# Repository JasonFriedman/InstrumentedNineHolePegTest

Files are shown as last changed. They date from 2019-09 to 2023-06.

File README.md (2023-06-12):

# InstrumentedNineHolePegTest
An instrumented version (i.e., with sensors) of the nine hole peg test

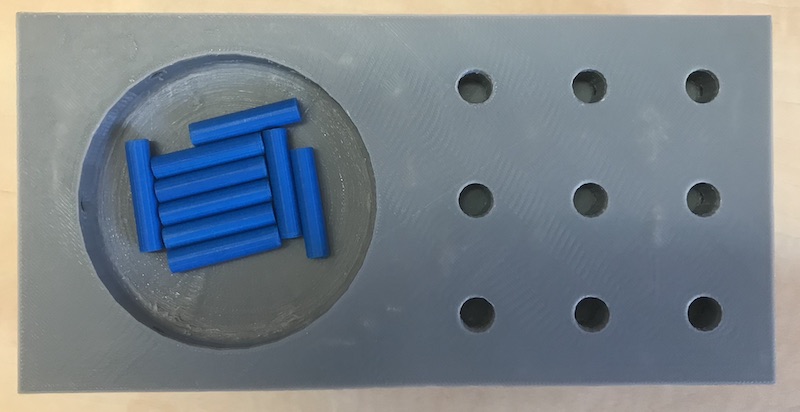
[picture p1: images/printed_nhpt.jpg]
Picture of the 3D printed device


Details about how to build the test can be found in the 
[wiki](https://github.com/JasonFriedman/InstrumentedNineHolePegTest/wiki)



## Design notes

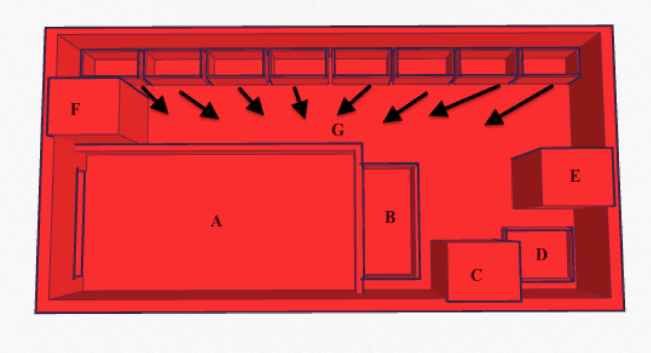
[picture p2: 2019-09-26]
images/base.png

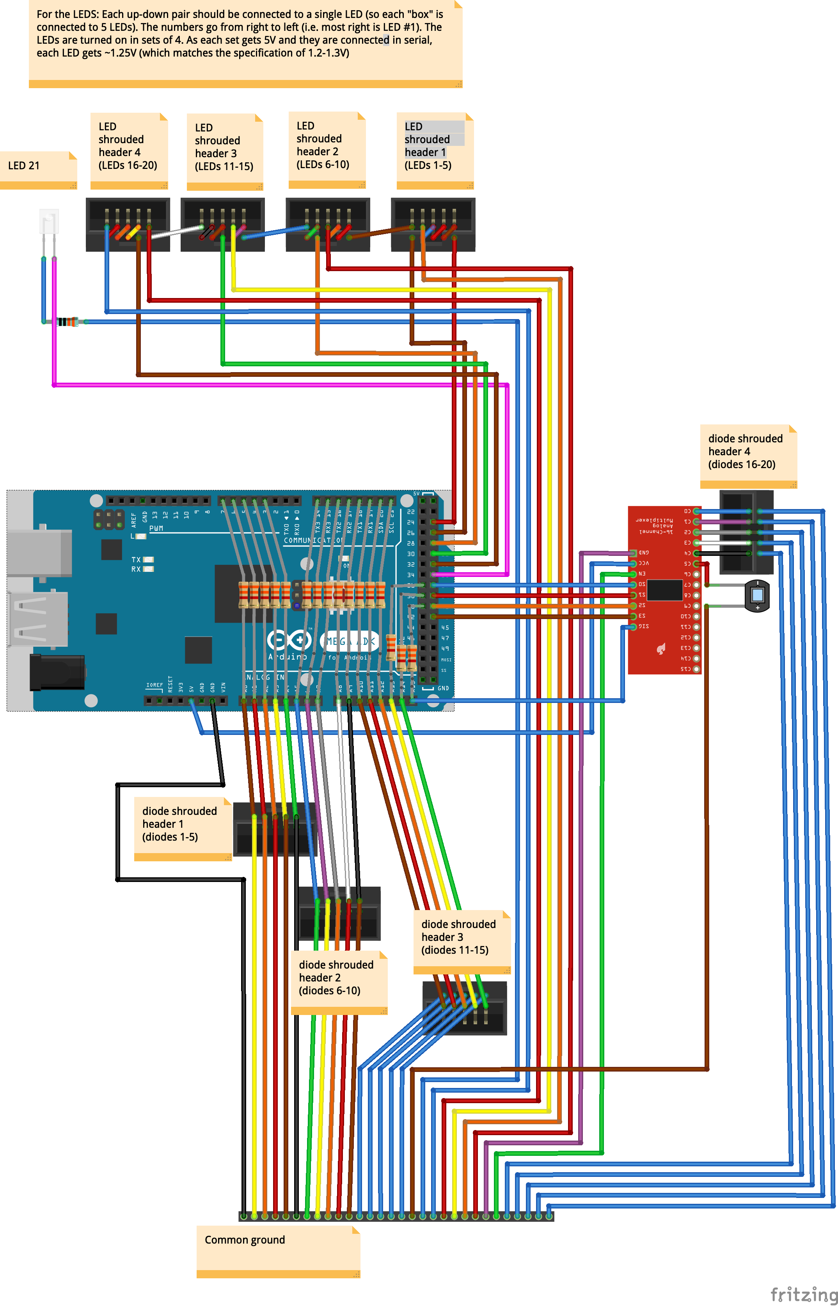
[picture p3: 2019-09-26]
images/NHPT_bb.png

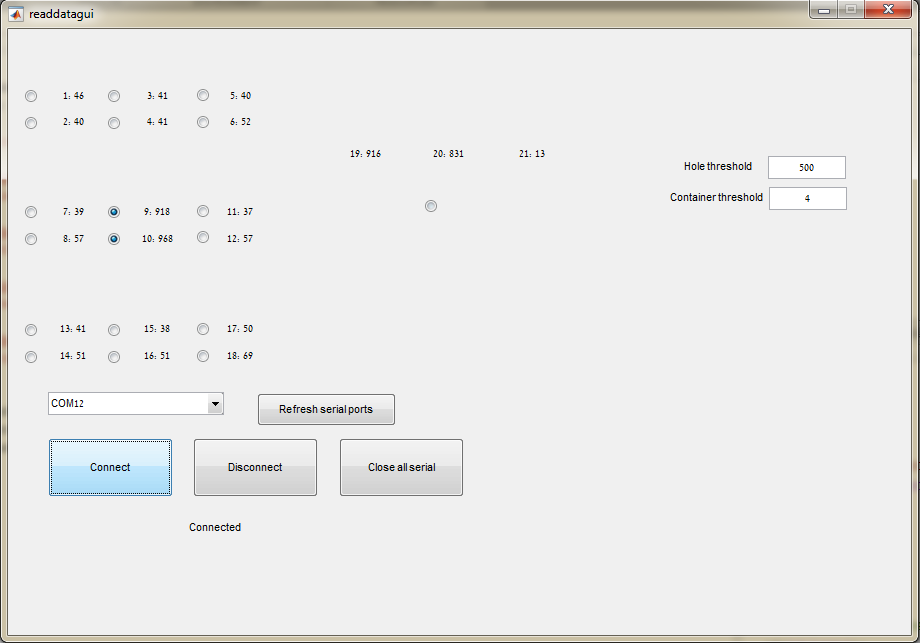
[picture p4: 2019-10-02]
images/readdatagui.png

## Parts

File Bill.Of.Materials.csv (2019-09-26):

Name | Quantity | Price for 1 unit (September 2019) | Total price (September 2019) | Link | Notes
Arduino Mega or Mega ADK | 1 | $38.95 | $38.95 | https://www.sparkfun.com/products/11061 | Need Mega so there will be enough pins
SparkFun Analog/Digital MUX Breakout - CD74HC4067 | 1 | $5.50 | $5.50 | https://www.sparkfun.com/products/9056 | There are not enough analog pins on the arduino so this allows connecting more
3mm 940nm LEDs infrared emitter and IR receiver diode | 21 pairs | $4.80 | $4.80 | https://www.ebay.com/itm/100pcs-3mm-940nm-LEDs-infrared-emitter-and-IR-receiver-diode-50pairs-diodes-/252112752434 | These require 1.2 - 1.3 V, so we connected 4 in serial to the 5V outputs
Ribbon wire cable - 10 wires | 15 ft | $4.95 | $4.95 | https://www.sparkfun.com/products/10647 | This 10 wires ribbon cable is used so that it can be easily used with the crimp connectors (next item)
Ribbon Crimp Connector - 10-pin (2x5, Female) | 8 | $0.50 | $4.00 | https://www.sparkfun.com/products/10650
2x5 Pin Shrouded Header | 8 | $1.50 | $12.00 | https://www.sparkfun.com/products/8506
Female 0.1" crimp pins (100) | 1 | $5.95 | $5.95 | https://www.pololu.com/product/1930
Male 0.1" crimp pins (100) | 1 | $7.95 | $7.95 | https://www.pololu.com/product/1931
Jumper wires - connected female to female 6" (pack of 20) | 2 packs | $1.95 | $3.90 | https://www.sparkfun.com/products/12796
Jumper wires - connected female to male 6" (pack of 20) | 2 packs | $1.95 | $3.90 | https://www.sparkfun.com/products/12794
Jumper wires - connected female to female 6" (pack of 20) | 2 packs | $1.95 | $3.90 | https://www.sparkfun.com/products/12795
3300 Ω = 3.3k Ω resistors | 50 | $1.08 | $1.08 | https://www.ebay.com/itm/100Pcs-1-4W-0-25W-Metal-Film-Resistor-1-1K-910K-Ohm-1K-10K-100K-47K-22K-33K/192901341321
330 Ω resistors | 5 | $0.95 | $0.95 | https://www.sparkfun.com/products/14490
Heat shrink |  | $7.95 | $7.95 | https://www.sparkfun.com/products/9353
3D printed base (to be printed using a 3D printer) | 1 |  |  | https://github.com/JasonFriedman/InstrumentedNineHolePegTest/raw/master/3D_printer_parts/base.stl
3D printed top (to be printed using a 3D printer) | 1 |  |  | https://github.com/JasonFriedman/InstrumentedNineHolePegTest/raw/master/3D_printer_parts/top.stl
3D printed peg (to be printed using a 3D printer) | 9 |  |  | https://github.com/JasonFriedman/InstrumentedNineHolePegTest/raw/master/3D_printer_parts/peg.stl

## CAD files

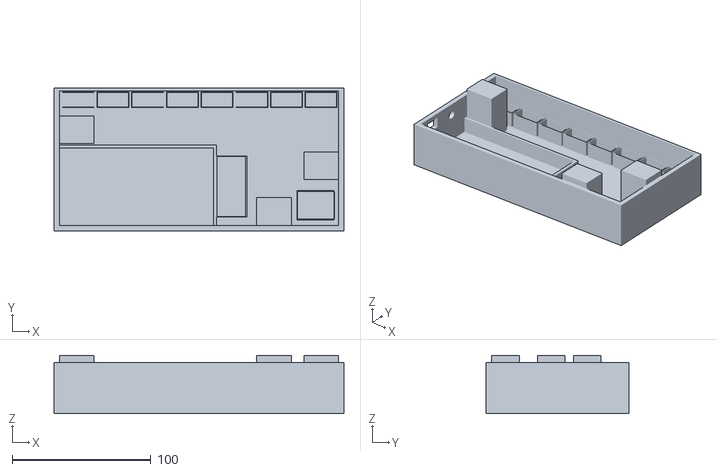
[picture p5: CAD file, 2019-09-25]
3D_printer_parts/base.stl
209.0 x 103.0 x 42.0

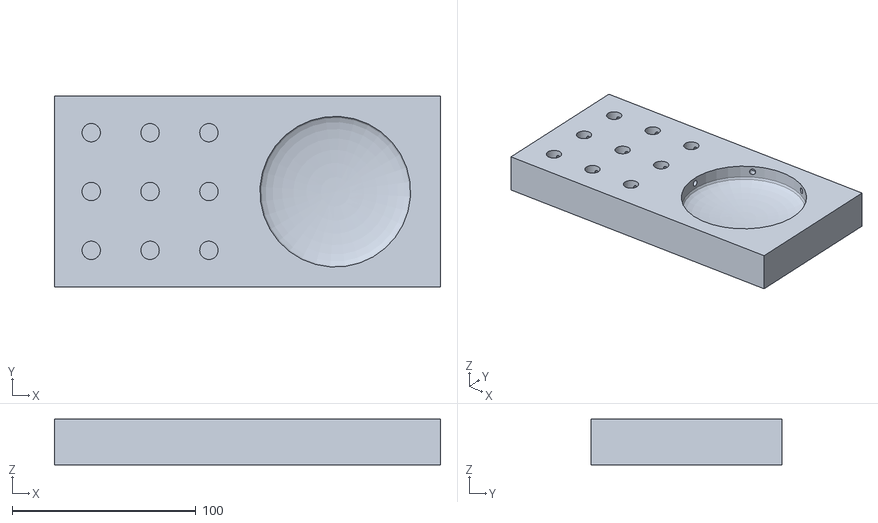
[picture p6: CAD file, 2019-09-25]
3D_printer_parts/top.stl
210.0 x 104.0 x 25.0

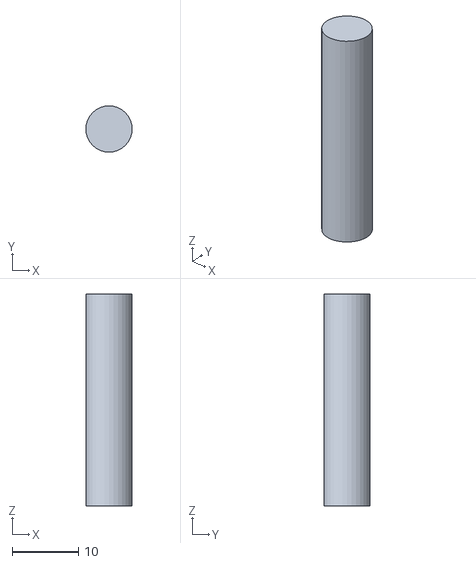
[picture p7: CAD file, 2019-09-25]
3D_printer_parts/peg.stl
7.00 x 7.00 x 32.0

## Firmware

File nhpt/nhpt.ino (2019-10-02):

// Code for running the instrumented nine hole peg test
// Full details for building the device can be found at https://github.com/JasonFriedman/InstrumentedNineHolePegTest

#include <Streaming.h>

int LEDs[] = {25, 27, 29, 31, 33, 35};

int diodes_5V[] =  { 7,  6,  5,  4,  3, 14, 15, 16, 17, 18,  19,  20,  21,  36, 38, 40};
int analogPins[] = {A0, A1, A2, A3, A4, A5, A6, A7, A8, A9, A10, A11, A12, A13, A14, A15};

int val_on[21];


int muxChannel[16][4] = { // From: http://bildr.org/2011/02/cd74hc4067-arduino/
  {0, 0, 0, 0}, //channel 0
  {1, 0, 0, 0}, //channel 1
  {0, 1, 0, 0}, //channel 2
  {1, 1, 0, 0}, //channel 3
  {0, 0, 1, 0}, //channel 4
  {1, 0, 1, 0}, //channel 5
  {0, 1, 1, 0}, //channel 6
  {1, 1, 1, 0}, //channel 7
  {0, 0, 0, 1}, //channel 8
  {1, 0, 0, 1}, //channel 9
  {0, 1, 0, 1}, //channel 10
  {1, 1, 0, 1}, //channel 11
  {0, 0, 1, 1}, //channel 12
  {1, 0, 1, 1}, //channel 13
  {0, 1, 1, 1}, //channel 14
  {1, 1, 1, 1} //channel 15
};

// Multiplexer pins
int S0 = 37;
int S1 = 39;
int S2 = 41;
int S3 = 43;

// 0 = off (no output), 1 = continuous output, 2 = only when requested
// Starts in mode 2
int mode = 2;

unsigned long lasttime = 0;
unsigned long lasttimesecs = 0;
int lasttimems = 0;

// Function definitions
void turnOnLEDsdiodes(int LED, int firstdiode, int lastdiode);
void turnOffLEDsdiodes(int LED, int firstdiode, int lastdiode);
void multiplexer(int channel);
void sendint(int val, int numPlacesBefore, bool trailingComma);

// the setup routine runs once when you press reset:
void setup() {
  // initialize the digital pin as an output.
  for (int i = 0; i <= 5; i++) {
    pinMode(LEDs[i], OUTPUT);
  }

  for (int i = 0; i <= 15; i++) {
    pinMode(diodes_5V[i], OUTPUT);
  }

  // Set multiplexer pins to output, and set them to 0
  pinMode(S0, OUTPUT); pinMode(S1, OUTPUT); pinMode(S2, OUTPUT); pinMode(S3, OUTPUT);
  digitalWrite(S0, 0); digitalWrite(S1, 0); digitalWrite(S2, 0); digitalWrite(S3, 0);

  Serial.begin(115200);
}

void loop() {
  int printdata = 0;
  // Read from the serial port, if it sent a "s", return a sample of data
  if (Serial.available()) {
    // Read the incoming byte
    int incoming = Serial.read();
    if (char(incoming) == '0') {
      mode = 0;
      Serial.println('0');
    } else if (char(incoming) == '1') {
      mode = 1;
      Serial.println('1');
    } else if (char(incoming) == '2') {
      mode = 2;
      Serial.println('2');
    } else if (mode == 2 && char(incoming) == 's') {
      printdata = 1;
    }
  }

  if (mode == 1) {
    printdata = 1;
  }

  if (printdata) {
    Serial.print("P");
    for (int i = 0; i <= 20; i++) {
      sendint(val_on[i], 4, 1);
    }
    // Send the time
    lasttimesecs = (lasttime / 1000) % 10000;
    lasttimems = lasttime % 1000;
    sendint(lasttimesecs, 4, 0);
    Serial << ".";
    sendint(lasttimems, 3, 0);
    Serial.println();
  }

  lasttime = millis();
  turnOnLEDsdiodes(0, 0, 3);
  for (int i = 0; i <= 3; i++) {
    val_on[i] = analogRead(analogPins[i]);
  }
  turnOffLEDsdiodes(0, 0, 3);

  turnOnLEDsdiodes(1, 4, 7);
  for (int i = 4; i <= 7; i++) {
    val_on[i] = analogRead(analogPins[i]);
  }
  turnOffLEDsdiodes(1, 4, 7);

  turnOnLEDsdiodes(2, 8, 11);
  for (int i = 8; i <= 11; i++) {
    val_on[i] = analogRead(analogPins[i]);
  }
  turnOffLEDsdiodes(2, 8, 11);

  turnOnLEDsdiodes(3, 12, 15);
  // Set the multiplexer for channel C0
  multiplexer(0);
  for (int i = 12; i <= 15; i++) {
    val_on[i] = analogRead(analogPins[i]);
  }
  // Don't turn off 15
  turnOffLEDsdiodes(3, 12, 14);

  // turn on LED 4 (diode 15 is already on)
  digitalWrite(LEDs[4], HIGH);
  for (int i = 1; i <= 4; i++) {
    // Set the multiplexer for channels C1,C2,C3,C4
    multiplexer(i);
    val_on[i + 15] = analogRead(analogPins[15]);
  }
  digitalWrite(LEDs[4], LOW);   // turn the LED off

  // turn on lone LED (diode 15 is already on)
  digitalWrite(LEDs[5], HIGH);
  // Set the multiplexer for the channel C5
  multiplexer(5);
  val_on[20] = analogRead(analogPins[15]);
  turnOffLEDsdiodes(5, 15, 15);
}

// Turn on the specified LED and diodes
void turnOnLEDsdiodes(int LED, int firstdiode, int lastdiode) {
  digitalWrite(LEDs[LED], HIGH);
  for (int i = firstdiode; i <= lastdiode; i++) {
    digitalWrite(diodes_5V[i], HIGH);
  }
}

// Turn off the specified LED and diodes
void turnOffLEDsdiodes(int LED, int firstdiode, int lastdiode) {
  digitalWrite(LEDs[LED], LOW);
  for (int i = firstdiode; i <= lastdiode; i++) {
    digitalWrite(diodes_5V[i], LOW);
  }
}

// Set the multiplexer to a given channel (between 0 and 15)
void multiplexer(int channel) {
  digitalWrite(S0, muxChannel[channel][0]);
  digitalWrite(S1, muxChannel[channel][1]);
  digitalWrite(S2, muxChannel[channel][2]);
  digitalWrite(S3, muxChannel[channel][3]);
}

// Send a fixed length integer through the Serial connection (padded with 0s at the beginning)
// numDigits - fixed number of digits to be send (0s will be added at the beginning)
// trailingComma - whether to add a comma after the number
void sendint(int val, int numPlacesBefore, bool trailingComma) {
  for (int k = numPlacesBefore - 1; k > 0; k--) {
    Serial << ( (val < pow(10, k)) ? "0" : "");
  }
  Serial << val;
  if (trailingComma) {
    Serial << ',';
  }
}

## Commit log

2019-09-25 STL files for the 3 parts
    [base.stl, peg.stl, top.stl]
2019-09-26 Added Bill of materials
    [Bill.Of.Materials.csv]
2019-09-26 Added arduino code and fritzing connection diagram
    [NHPT.fzz]
2019-10-02 Sample image of using readdatagui matlab script
2019-10-02 Updated arduino file (including timestamp)
2019-10-02 Include image of the printed test
